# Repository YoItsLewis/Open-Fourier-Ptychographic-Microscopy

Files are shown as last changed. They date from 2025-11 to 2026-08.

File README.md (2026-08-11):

# Open Fourier Ptychographic Microscopy (OpenFPM)
**Open Fourier Ptychographic Microscopy (OpenFPM)** is a low-cost, modular, and open-source platform for Fourier Ptychographic Microscopy (FPM). It combines programmable LED illumination, 3D-printed optomechanical components, and computational reconstruction to enable high-resolution, wide field-of-view imaging using accessible hardware. The microscope architecture is based on version 7 of the OpenFlexure Project.

## Overview
Traditional FPM systems are typically implemented by retrofitting LED arrays onto commercial microscopes or through bespoke laboratory setups. These approaches can limit reproducibility, accessibility, and system-level optimisation. 

**OpenFPM addresses this by providing a fully integrated, purpose-built system**, in which optics, illumination, mechanics, and control software are designed to work together as a unified platform.

The system supports:
- Multi-angle programmable illumination
- Synthetic numerical aperture enhancement
- Digital aberration correction
- Multimodal imaging (e.g. brightfield, darkfield, Rheinberg contrast)

By leveraging open-source designs and widely available components, OpenFPM lowers the barrier to entry for computational microscopy in: 
- Research
- Education
- Resource-limited environments

## Pre-print Paper and Citation
Our 2026 bioRxiv preprint is available:

Walker, Lewis D., et al. 
"Open Fourier Ptychographic Microscopy (OpenFPM)" 
bioRxiv (2026): 2026-03

## Build Your Own OpenFPM system
<p align='center'>
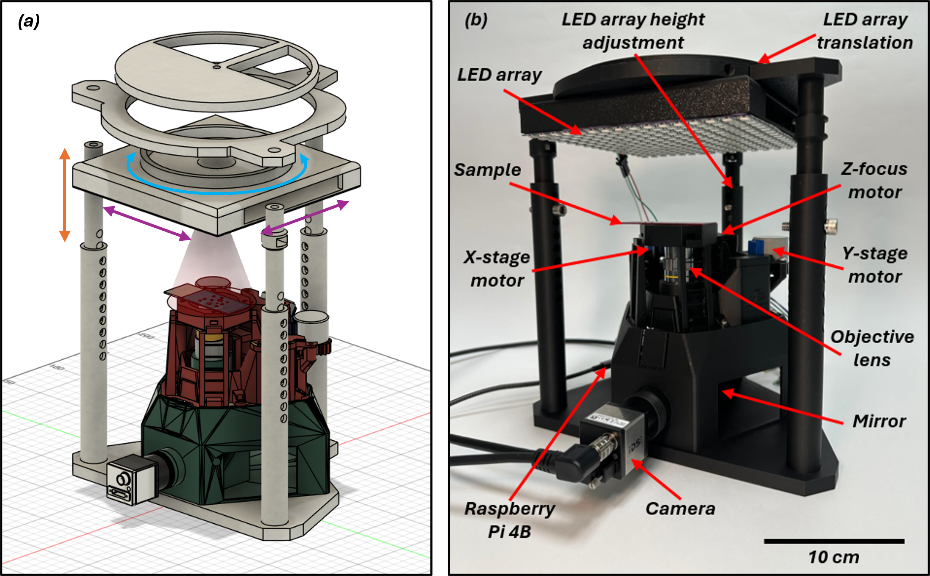
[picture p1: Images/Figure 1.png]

</p>

### Hardware

All 3D-printed components were fabricated using fused deposition modelling (FDM) with matte black polylactic acid (PLA) filament at a 0.4 mm layer height. Default print settings were used, with tree supports applied where required.

We found the [Bambu Labs P1S 3D Printer](https://uk.store.bambulab.com/products/p1s?id=578772891943051270) to be reliable for producing the components.

### Material Costs

Estimated material costs for building an OpenFPM system (excluding tools and general IT equipment):

| Parts | Purpose | Source | Quantity | Price (£) |
|-----|-----|-----|-----|-----|
| **Electronic Components** |
| Raspberry Pi 4 Model B Starter Kit (1GB) | Microcomputer for controlling the microscope | [The Pi Hut](https://thepihut.com/products/raspberry-pi-starter-kit?srsltid=AfmBOoqbFpfRUvJug9U0IUKZXNz2ZsnnAsgzD-O2ssctK8kTpJ7MEXZv&variant=41173475754179) | 1 | ~£57 |
| 28BYJ-48 5V Stepper Motor + Driver Board | Objective focus and X-Y sample translation | [Amazon](https://www.amazon.co.uk/GeeekPi-Stepper-28BYJ-48-Uln2003-Compatible/dp/B087BYKB6T/ref=sr_1_5?dib=eyJ2IjoiMSJ9.tpKbALur4RZR5JjIbrZBahg9M0IhaDgmiF7VwBWE_2lsTL00-iRC6xXIvnyfChnaYqPoV9Gr50YNRAiiWclIkc7meNSNdmMirNrMPg_gOMrreA9ZntPfVBQ38vUR9fwi93x8wK9a9-xv7wTnYonW1l5yaqqH8dDyoqPMSYfvQgSfoi7agcg3Q4DXaJho1xlHV60y0XfS1d2ZRnEMOHDfPPFEu1HbcgymNHAHrIat6Jai5Hy_woxu5Wi1DnVFxtKRGXrG9qPlf7OP2aix-48fc58KT13RH6gw9dvW76QfDPg._fRZJClR4FFzt0LQ7L6sIkDKB9mwDvTVIwPNkDp-gEc&dib_tag=se&keywords=28byj-48&qid=1773853029&sr=8-5) | 1 | ~£16 |
| WS2812B RGB 16x16 LED Array | Microscope illumination source | [Amazon](https://www.amazon.co.uk/BTF-LIGHTING-Individual-Addressable-Flexible-Controllers/dp/B088K1JH6X/ref=sr_1_4?crid=1TDCCR1PVHEZI&dib=eyJ2IjoiMSJ9.BlBbfjaxQD81QRlFc0RoykGyvNqepSEBWBUXSh5dhH8Izaq5I3eHLzQNwcP58zJ_g5KJcmAz3sXc5WHSyN3tFMFqY885Ji_6wpYi1NJLEjbaBzJerwrchq3Al4w8YoxB44xzRurl0KOIqh-5-MLe0q_TGN8MHpB84Jl03lWM88kHzF7ABw2D_dwZOi-cpTNZaxy0pDkv0YXhD4YJeiqqaFl3o17sfhu8GvuNenMw-57pwuYcKO2ADKH5zCnCxQtYtTxeWC3wZmMnI0opGIlZ_wdnl_BQJ4-rvEX3ecfqd6A.ILqKG4o1fKNMmcr2hGjSUMYwglu0uDxfSaB0AR59xHk&dib_tag=se&keywords=led%2Barray&qid=1773851490&s=kitchen&sprefix=led%2Barray%2Ckitchen%2C222&sr=1-4&th=1) | 1 | ~£20 |
| Breadboard and Jumper Wires Kit | Wiring for connecting the microcomputer to the LED array + Motors | [Amazon](https://www.amazon.co.uk/HUAREW-Breadboard-Jumper-Include-Points/dp/B0B5TCKTQH/ref=sr_1_4_sspa?crid=314GBN29Q2J8Q&dib=eyJ2IjoiMSJ9.Vdt6Ti1-DwLZVl5Jd0sx8KltvLq3nGuI3O04CljjMjJocwzI61z4BB8c2a6rk0_9YaFVxERGaFBxc0RotFdqHZlzmlmX0Bp-n_uB6315HeygDOw5QO-6VEgO0mXQDr6mDOv0xnvJ4iTOfin41Tiof4i14ME5M7KTHz8C8Um_5GoPDg4zJ0oTeF5nXYIctct5aNjJOGhbHd2HcHNLUlW4ldUbhzsSWMjL6NehSN-cv4WeTMtcGuIXSskGMmhh-G8XeVrsZpbGsGJ7sSK_u00s51z4WUAfj5VZ1297tedRsZ0.nCFNU3pLaWR8MUiCFS34yDLuV5LY6le9KtSD54dFcJU&dib_tag=se&keywords=electronics+breadboard&qid=1773851170&sprefix=electronics+breadboard%2Caps%2C253&sr=8-4-spons&aref=b7CJuJoBlm&sp_csd=d2lkZ2V0TmFtZT1zcF9hdGY&psc=1) | 1 | ~£13 |
| Monochromatic Camera (c-mount) | Acquiring image data | [Edmund Optics](https://www.edmundoptics.co.uk/c/cameras/1012/#27915=27915_s%3AC-Mount&397021=397021_s%3AMonochrome&29401=29401_s%3AIDS) | 1 | ~£300 (Based on iDS camera) |
| USB 3.0 A to Right-Angle Micro B Cable | Provides power to the camera and transfers image data | [Thorlabs](https://www.thorlabs.com/item/CABU32) | 1 | ~£17 |
| 8 Pin Hirose Camera Cable | Cable for triggering camera from microcomputer | [Amazon](https://www.amazon.co.uk/Alvins-Cables-HR25-7TP-8S-Imaging-Industrial/dp/B08FD6B262?source=ps-sl-shoppingads-lpcontext&ref_=fplfs&th=1) | 1 | ~£25 |
| **Total** |||| ~ £448 |
| **Optomechanical Components** |
| Finite Conjugate Objective Lens | Objective lens for microscope | [Edmund Optics](https://www.edmundoptics.com/f/commercial-grade-standard-microscope-objectives/12253/) | 1 | ~£152 (10x/0.25 Plan) |
| ⌀1" Protected Aluminum Mirror | Redirect light path onto camera sensor | [Thorlabs](https://www.thorlabs.com/item/PF10-03-G01) | 1 | ~£50 |
| M6 x 16 mm | Screw for combining the LED box hat to the LED box holder | | 1 | |
| M6 x 20 mm | Screws, washers and nuts for combining external post to microscope base plate | | 3 | |
| M6 x 25 mm | Screws for pin and hole system | | 3 | |
| M6 x 30 mm | Screws and nuts for combining internal post to LED canopy | | 3 | |
| **Total** |||| ~£202 |
| **Overall Total** |||| ~£650 |

## Assembly Instructions

OpenFPM assembly guide can be found [here](https://github.com/YoItsLewis/Open-Fourier-Ptychographic-Microscopy/tree/main/Assembly%20Instructions).

OpenFlexure microscope assembly instructions can be found [here](https://build.openflexure.org/openflexure-microscope/v7.0.0-beta5/high_res_microscope.html). 

## Software

The OpenFPM software provides control of illumination, acquisition, and mechanical positioning via a Raspberry Pi-based graphical user interface (GUI).
- LED control using WS2812B NeoPixel interface
- Motor control for focus and stage translation
- Programmable illumination sequences for FPM acquisition

[NeoPixel](https://core-electronics.com.au/guides/fully-addressable-rgb-raspberry-pi/) setup guide.

OpenFPM [Control software](https://github.com/YoItsLewis/Open-Fourier-Ptychographic-Microscopy/tree/main/Software).

## Datasets

Due to file size constraints, example datasets are hosted externally:
- Siemen star (Red illumination) 
- Blood smear (RGB 3-channel illumination)

Available via the [Strathclyde Data Repository](https://pureportal.strath.ac.uk/en/persons/lewis-walker-2/).

## License

Original OpenFPM software, documentation, and custom files in this repository are released under the MIT License unless otherwise stated.

Certain hardware components are based on or compatible with the OpenFlexure Project. Original OpenFlexure hardware designs are licensed separately under CERN-OHL-S.

## Acknowledgements

OpenFPM builds upon foundational contributions from the Fourier Ptychographic Microscopy community and the OpenFlexure Project. OpenFlexure source files and licence information: https://gitlab.com/openflexure

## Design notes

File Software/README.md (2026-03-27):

# Software

This folder contains the software used to operate the OpenFPM microscope system, including microscope control, illumination and camera sequencing, motorised positioning, and optical alignment support.

### OpenFPM Control GUI

The OpenFPM control software provides a graphical user interface (GUI) for controlling the programmable LED illumination and microscope translation hardware.

### Features

#### LED Illumination Control

- Support for a 16x16 WS2812B LED array
- Adjustable:
  - LED colour
  - LED brightness
- Visual 16x16 LED grid interface

#### Timing

- User-defined timing parameters for image acquisition:
  - Exposure time (ms) - LED on duration
  - Capture time (ms) - LED off duration

#### Illumination Patterns

Predefined and custom illumination patterns are supported.

- Hold modes
  - Brightfield (BF)
  - Darkfield (DF)
- Triggered acquisition modes
  - Central 9 LEDs (3 LED diameter circle)
  - 69  LEDs (9 LED diameter circle)
  - 177 LEDs (15 LED diameter circle)

Users may also define custom LED illumination patterns directly in the code.

#### Motor Control

Integrated manual control of microscope motion:
- Z-axis focus
- X-axis stage translation
- Y-axis stage translation

#### Image of on-screen GUI

<p align='center'>
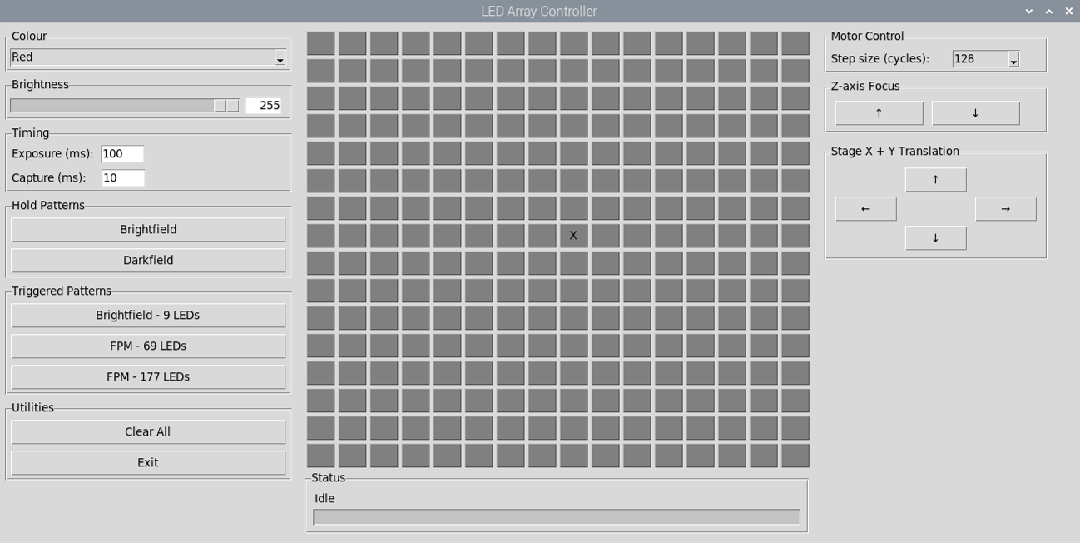
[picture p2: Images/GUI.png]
  
</p>

### Live FFT Alignment Support

OpenFPM incorporates a translational LED illuminator, allowing the user to manually align the LED array with the microscope optical axis for improved reconstruction quality.

To support this process, the system uses a high-contrast sample and live Fourier-space observation of the coherent brightfield passbands. This enables the user to visually assess whether the central LED is correctly aligned to the optical axis.

This alignment workflow is supported using a live on-screen FFT display in FIJI, adapted from the macro shared by Nicolás De Francesco [1].

Live FFT visualisation helps the user:
- Identify off-axis illumination
- Observe coherent passband displacement
- Manually correct LED array alignment
- Improve reconstruction consistency and quality

Below is an example showing the central LED:
- Off-axis (uncorrected) position
- On-axis (corrected) psoition

<p align='center'>
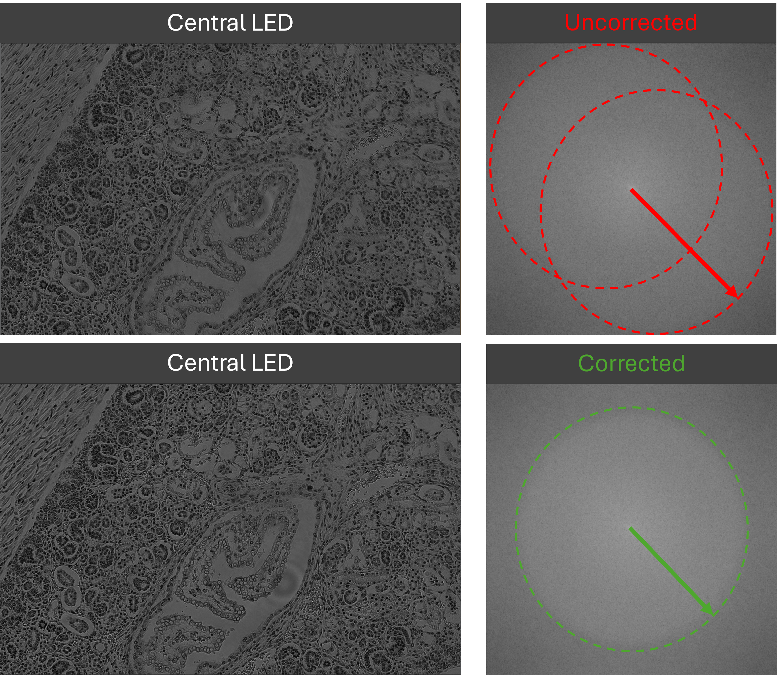
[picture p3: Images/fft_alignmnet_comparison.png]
  
</p>

### FIJI Macro Reference
Nicolás De Francesco,
“Is live FFT of an ROI on screen possible?”
Image.sc Forum, November 2019.
https://forum.image.sc/t/is-live-fft-of-an-roi-on-screen-possible/31026/4
Accessed: March 2026.

### Notes
- This software was developed for use with the OpenFPM hardware platform and may require modification for alternative hardware configurations.
- Custom illumination sequences and acquisition routines can be adapted within the source code depending on the desired imaging protocol.

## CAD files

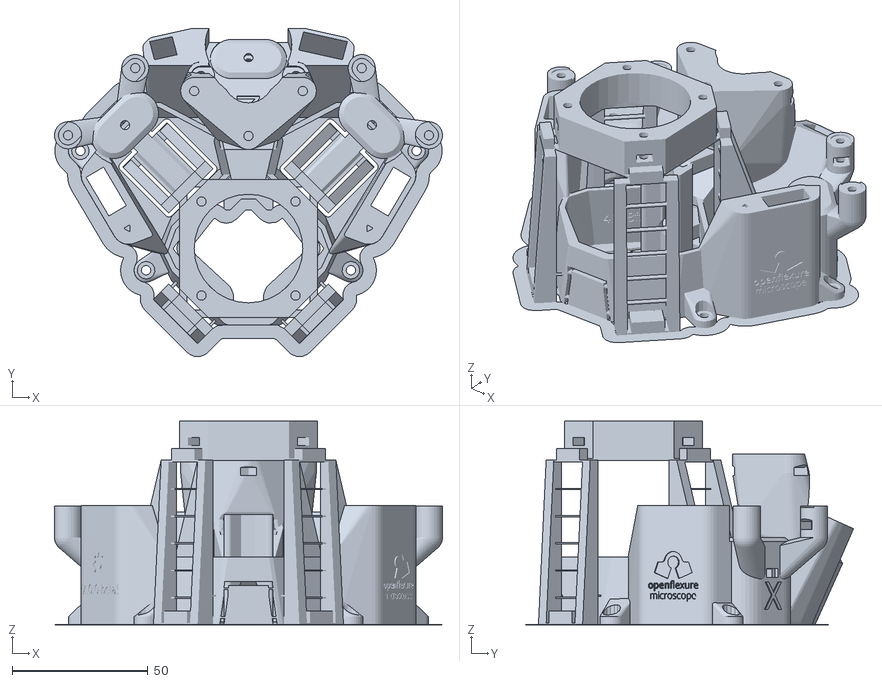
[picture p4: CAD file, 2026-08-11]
3D Printing Files/STL Files/OpenFlexure_main_body.stl
142.9 x 120.9 x 75.0

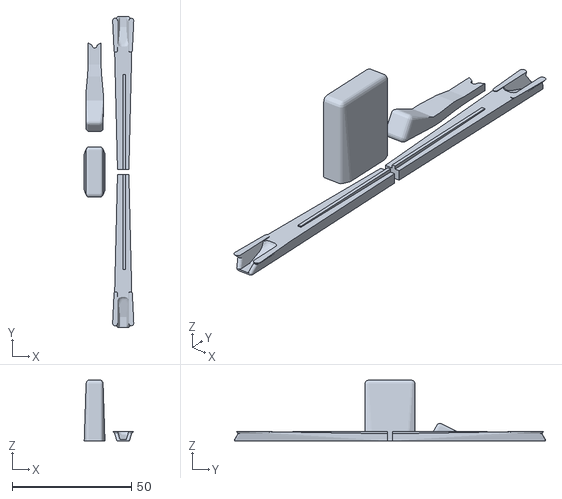
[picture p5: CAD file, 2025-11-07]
3D Printing Files/STL Files/OpenFlexure_actuator_assembly_tools.stl
20.8 x 130.5 x 25.5

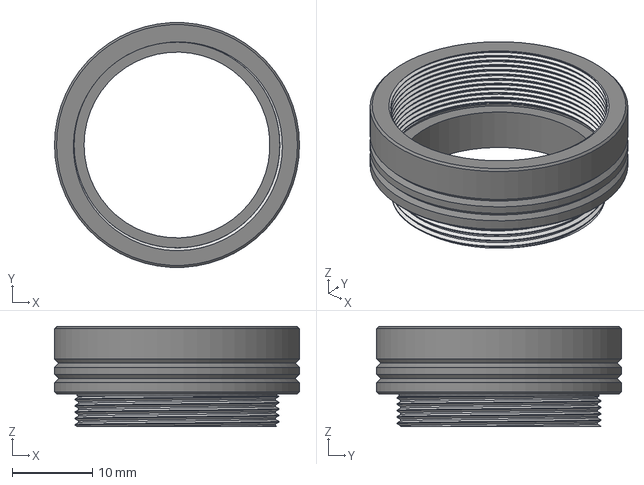
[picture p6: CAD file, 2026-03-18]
3D Printing Files/STEP Files/Camera Adapter.step
30.5 x 30.4 x 12.4 mm

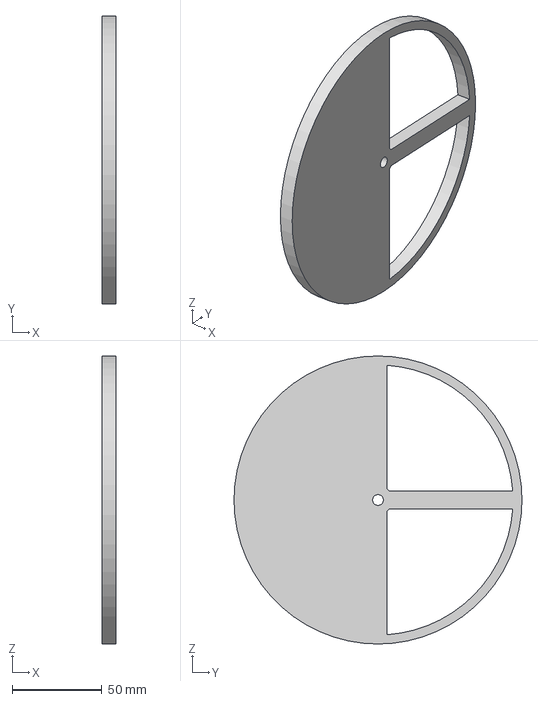
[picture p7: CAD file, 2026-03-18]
3D Printing Files/STEP Files/LED Box Hat.step
8.00 x 160.0 x 160.0 mm

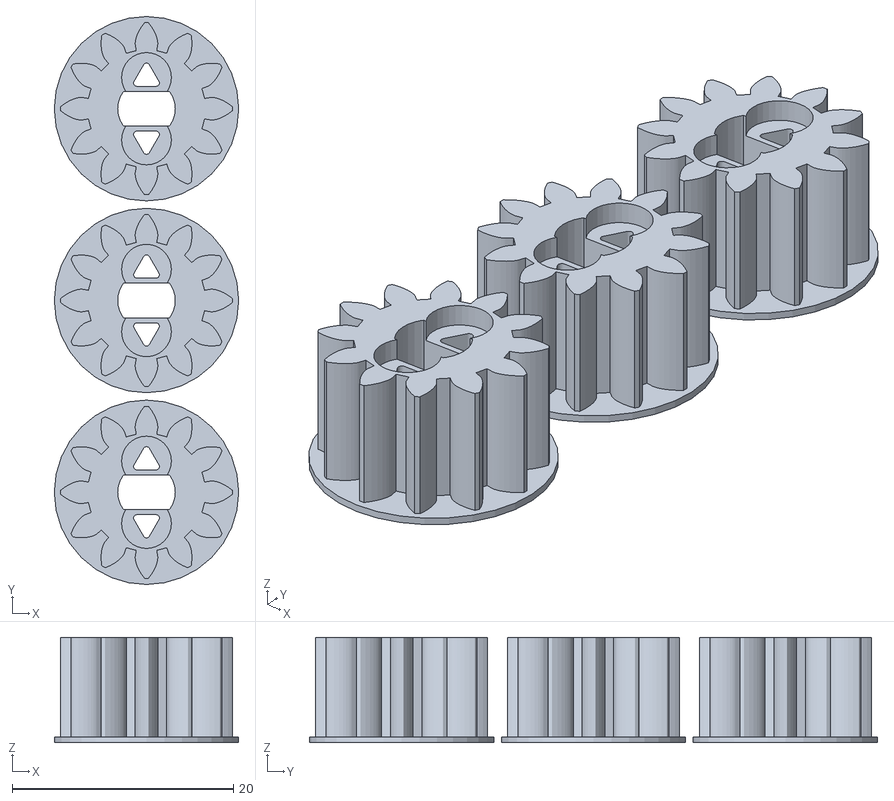
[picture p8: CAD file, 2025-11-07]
3D Printing Files/STL Files/OpenFlexure_small_gears.stl
16.7 x 51.3 x 9.50

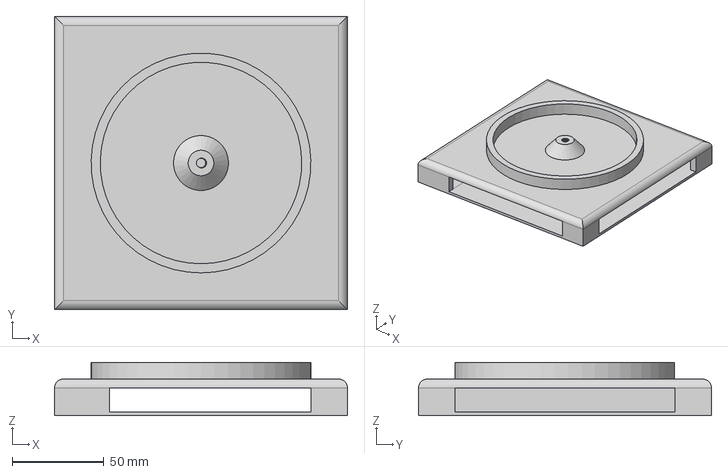
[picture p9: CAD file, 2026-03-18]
3D Printing Files/STEP Files/LED Box Holder.step
160.0 x 160.0 x 29.0 mm

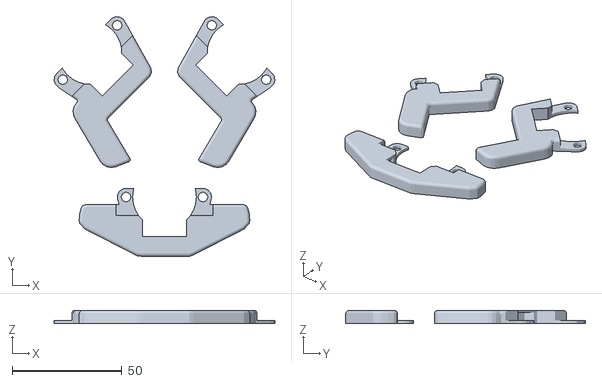
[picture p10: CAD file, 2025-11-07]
3D Printing Files/STL Files/OpenFlexure_cable_tidies.stl
100.6 x 109.1 x 6.03

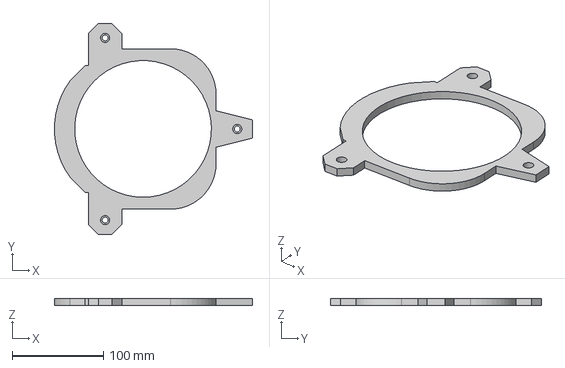
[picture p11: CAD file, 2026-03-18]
3D Printing Files/STEP Files/LED Canopy.step
217.3 x 232.0 x 8.00 mm

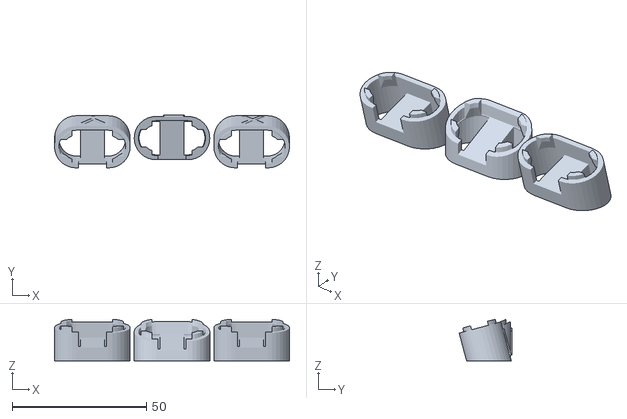
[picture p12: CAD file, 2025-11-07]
3D Printing Files/STL Files/OpenFlexure_feet.stl
87.6 x 19.7 x 15.5

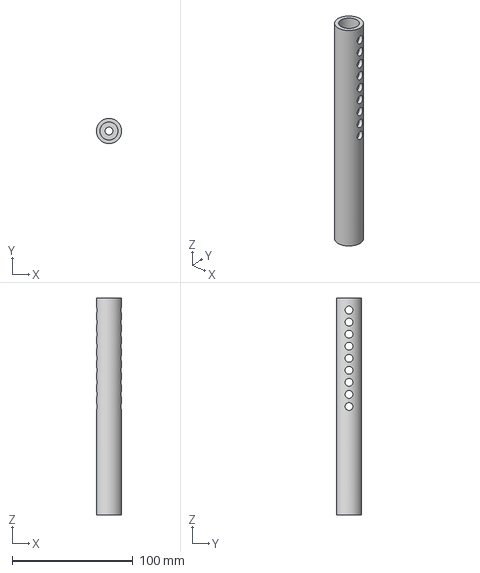
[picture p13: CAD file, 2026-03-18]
3D Printing Files/STEP Files/External Post.step
21.0 x 21.0 x 180.0 mm

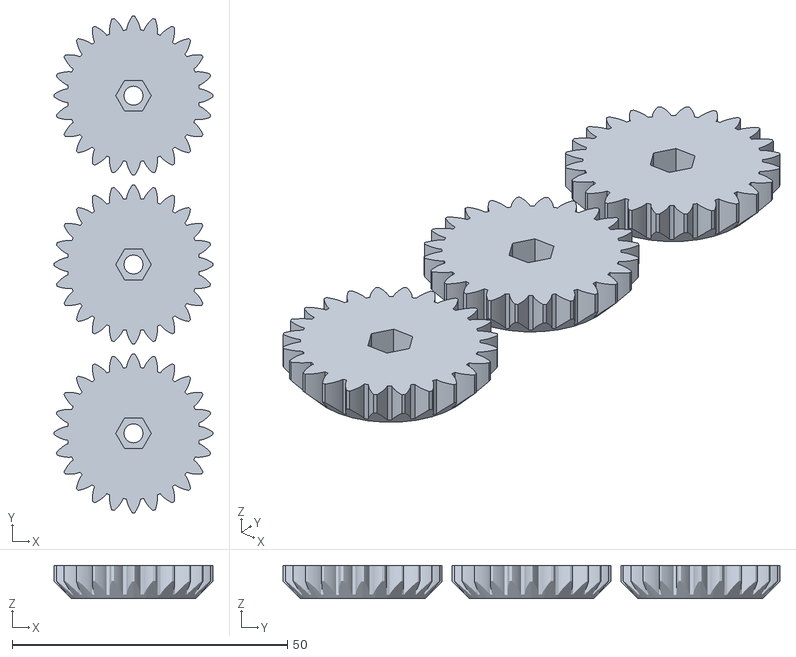
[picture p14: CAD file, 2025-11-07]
3D Printing Files/STL Files/OpenFlexure_large_gears.stl
28.9 x 90.2 x 6.00

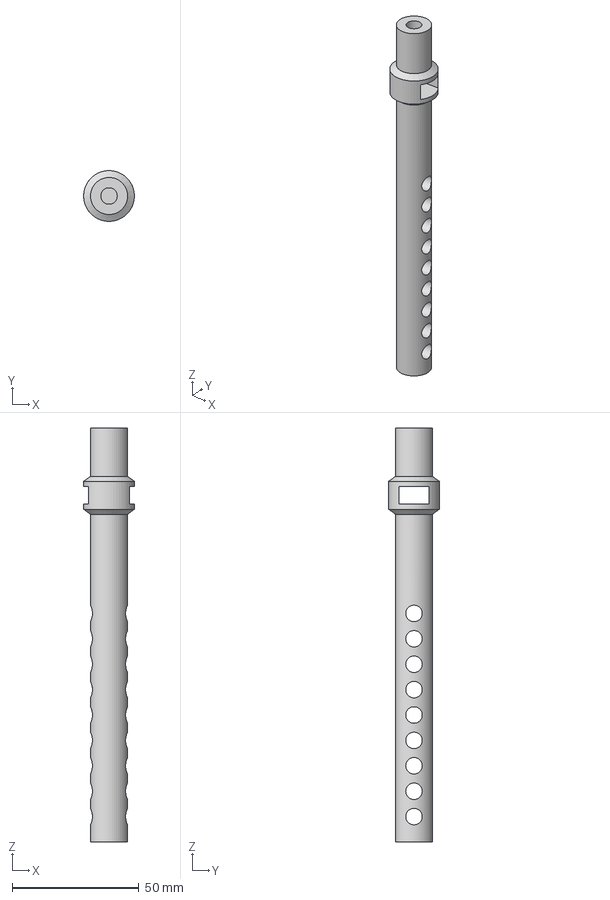
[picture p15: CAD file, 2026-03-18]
3D Printing Files/STEP Files/Internal Post.step
20.0 x 20.0 x 163.0 mm

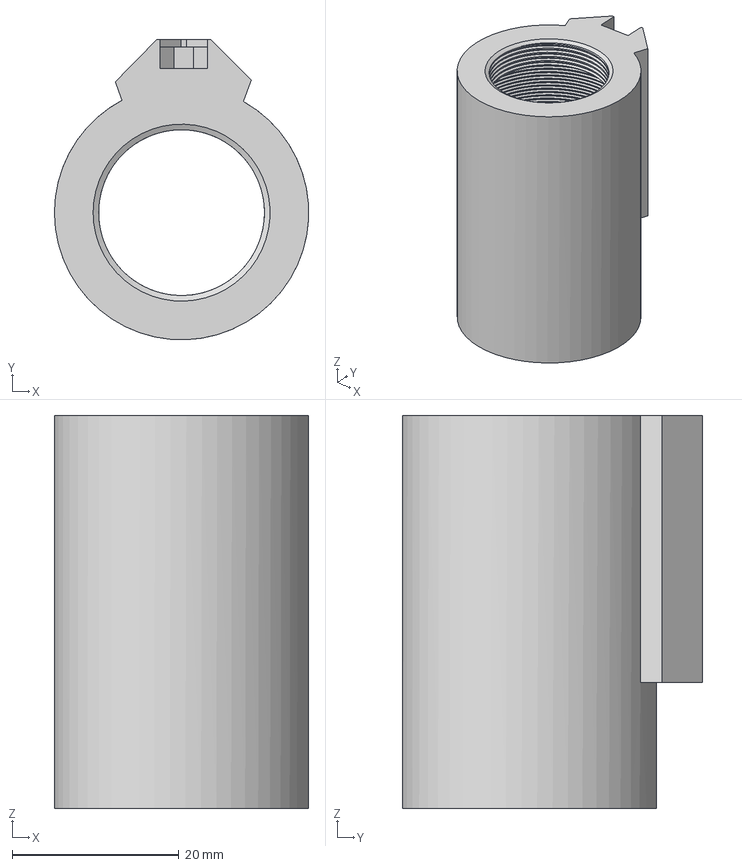
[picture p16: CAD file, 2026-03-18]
3D Printing Files/STEP Files/Objective Lens Holder.step
30.5 x 36.0 x 47.1 mm

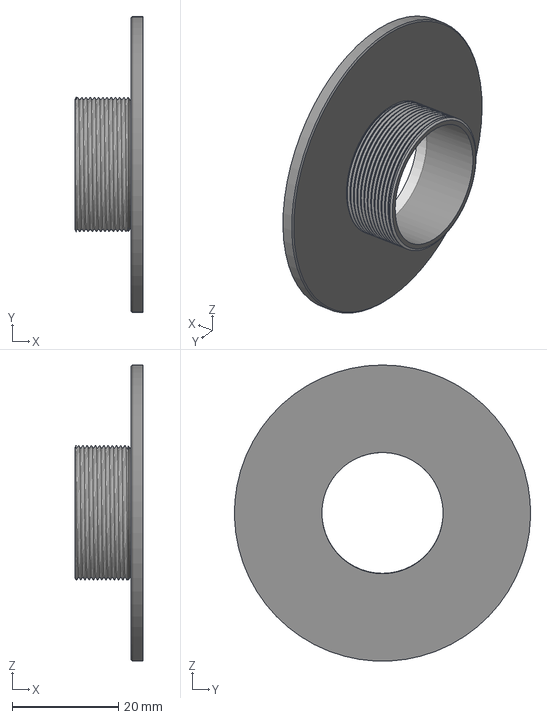
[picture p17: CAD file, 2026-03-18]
3D Printing Files/STEP Files/C mount Mirror Cover.step
12.9 x 55.9 x 55.8 mm

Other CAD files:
3D Printing Files/STEP Files/Microscope Base Plate.step
3D Printing Files/STEP Files/OpenFlexure Stand with Mirror Holder.stl
3D Printing Files/STEP Files/Hex Nut Tool.step
3D Printing Files/F3D Files/C mount Mirror Cover.f3d
3D Printing Files/F3D Files/Camera Adapter.f3d
3D Printing Files/F3D Files/External Post.f3d
3D Printing Files/F3D Files/Hex Nut Tool.f3d
3D Printing Files/F3D Files/Internal Post.f3d
3D Printing Files/F3D Files/LED Box Hat.f3d
3D Printing Files/F3D Files/LED Box Holder.f3d
3D Printing Files/F3D Files/LED Canopy.f3d
3D Printing Files/F3D Files/Microscope Base Plate.f3d
3D Printing Files/F3D Files/Objective Lens Holder.f3d
3D Printing Files/F3D Files/OpenFlexure Stand with Mirror Holder.f3d
3D Printing Files/STL Files/C mount Mirror Cover.stl
3D Printing Files/STL Files/Camera Adapter.stl
3D Printing Files/STL Files/External Post.stl
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

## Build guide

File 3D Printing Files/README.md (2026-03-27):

# 3D Printing Files

This directory contains the complete set of 3D design files for the OpenFPM microscope components. The files are provided in multiple formats to support a range of workflows, from direct 3D printing to further design modification and customisation.

### Folder Structure

The files are organised into three subfolder:

- F3D/
  - Native Autodesk Fusion 360 design files.
  - These are fully parametric and intended for users who wish to modify or adapt the designs.

- STEP/
  - Standard CAD exchange files (.step).
  - Suitable for use in a wide range of CAD software for inspection, modification, or integration into other assemblies.

- STL/
  - Mesh files for direct 3D printing.
  - These are ready to slice and can be used with most 3D printing software. (e.g. Bambu Studio, LycheeSlicer).

### Usage 

- For direct printing, use the files in the STL/ folder.
- For design modification or customisation, use the F3D/ or STEP/ files depending on your preferred CAD software.

### Notes

- All  components are designed to be compatible with the OpenFPM system architecture.
- Print settings (e.g. material, infill, layer height) may be adjusted depending on your printer and desired mechanical performance.
- Some parts may require support structures depending on orientation, this can usually be auto-checked in slice software.

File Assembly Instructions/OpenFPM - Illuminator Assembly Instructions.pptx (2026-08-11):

## OpenFPM: Illuminator Assembly Instructions

- Lewis Walker
- University of Strathclyde, Glasgow, Scotland
- Last Edited: 11th August 2026

## Components

Here we provide a list of the components (and their quantity) required to assemble the illuminator:

3D Printed Components:
- External post (x3)
- Internal post (x3)
- LED box hat (x1)
- LED box holder (x1)
- LED canopy (x1)
- Microscope base plate (x1)
- Hex Nut Tool (x1) - Tool
Metal Components:
- M6x16 mm bolt (x1)
- M6x20 mm bolt (x3)
- M6x25 mm bolt (x3)
- M6x30 mm bolt (x3)
- M6 nuts (x6)
Consumables + Tools
- Super-glue
- 5 mm hex key M6 tool
- 2.5 mm hex key M3 tool

## Parts I

From Left to Right on the image
Top:
- LED box hat (x1)
- LED box holder + LED array (under) (x1)
- Internal post (x3)
- External post (x3)
Bottom:
- LED canopy (x1)
- Microscope base plate (x1)
- Hex Nut Tool (x1)

## Parts II

Consumables + Tools:
- Super-glue
- 5 mm hex key M6 tool
- 2.5 mm hex key M3 tool
Optional:
- 3D printed bolt measuring tool
Metal components:
- M6 nuts (x6)
- M6x30 bolt mm (x3)
- M6x25 bolt mm (x3)
- M6x20 bolt mm (x3)
- M6x16 bolt mm (x1)

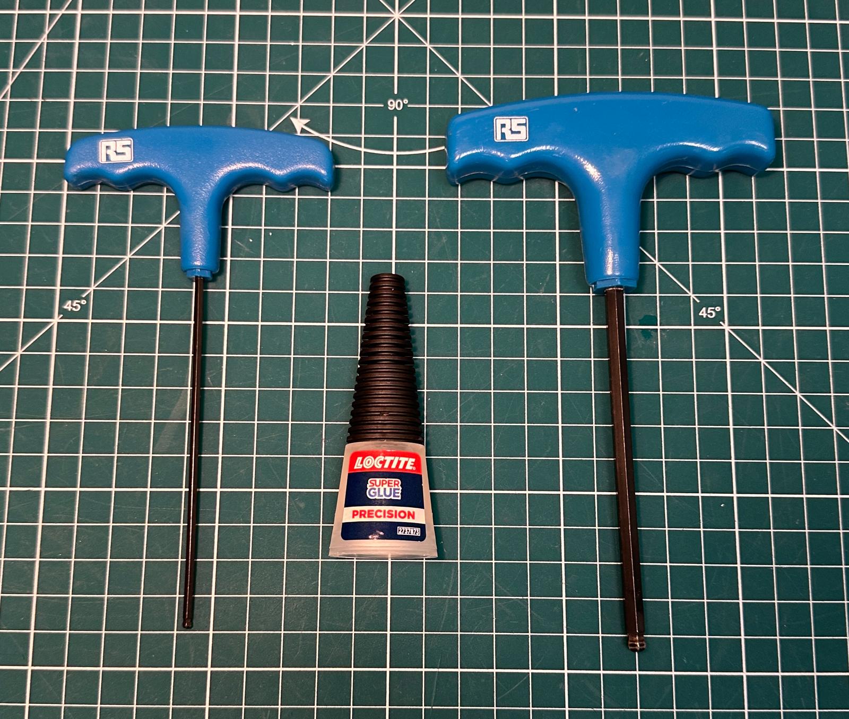
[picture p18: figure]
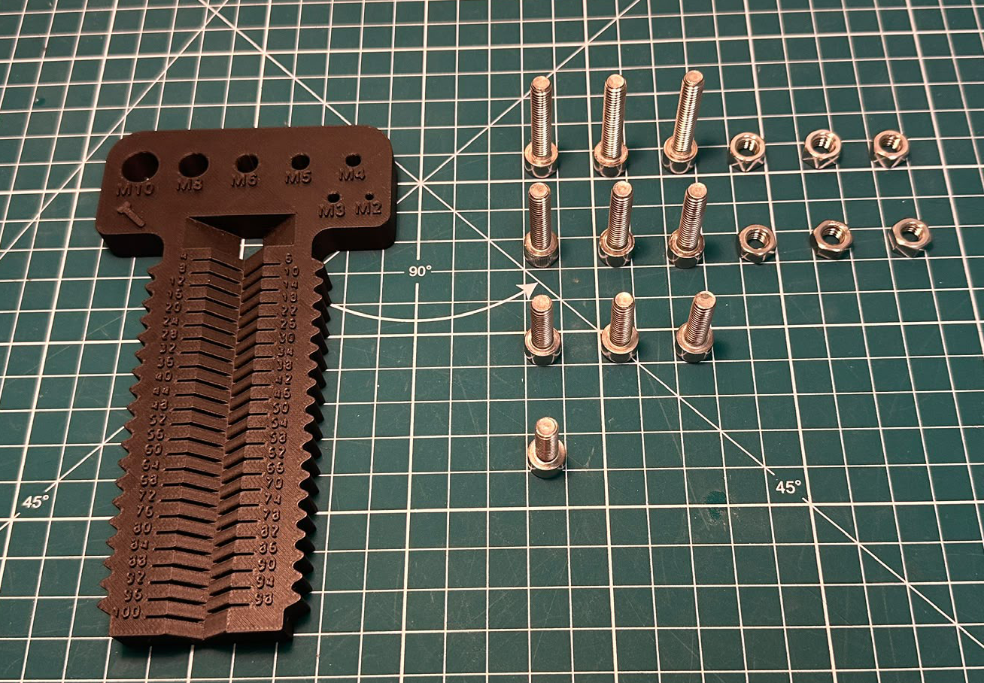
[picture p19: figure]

## Step 1

What you will need:
- LED box holder
- LED array
- Super-glue
TODO:
1. Thread LED wires through the square holes in the 3D printed box. Position the LED array to the edges of the box and superglue along the edges and the middle to ensure good contact.
2. Place upside-down on a flat surface and leave to dry.

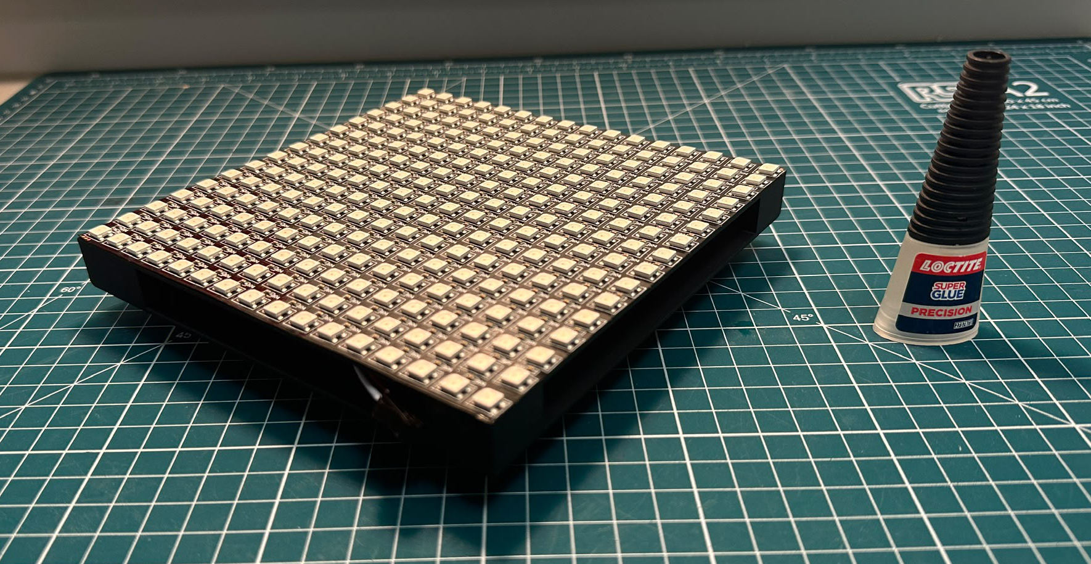
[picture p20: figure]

## Step 2(a)

What you will need:
- External posts
- Microscope base plate
- Hex nut tool
- M6x25 mm bolts (x3)
- M6 nuts (x3)

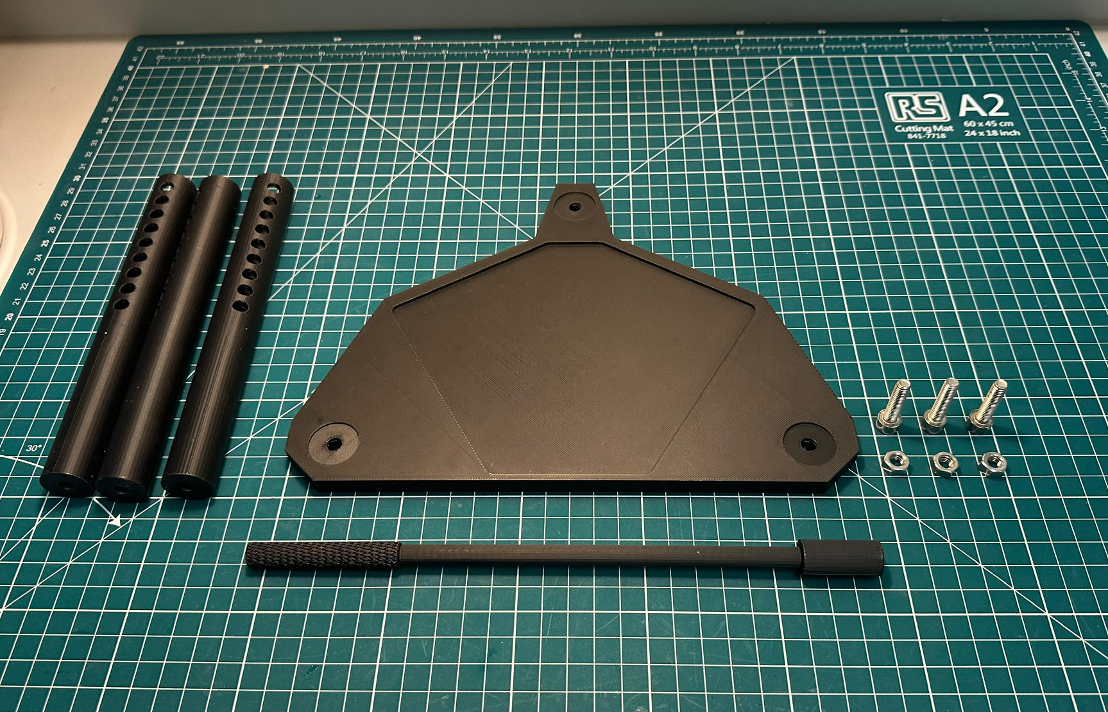
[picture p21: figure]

## Step 2(b)

TODO:
1. Place the 3 M6x25 mm bolts through the bottom of the microscope base plate.

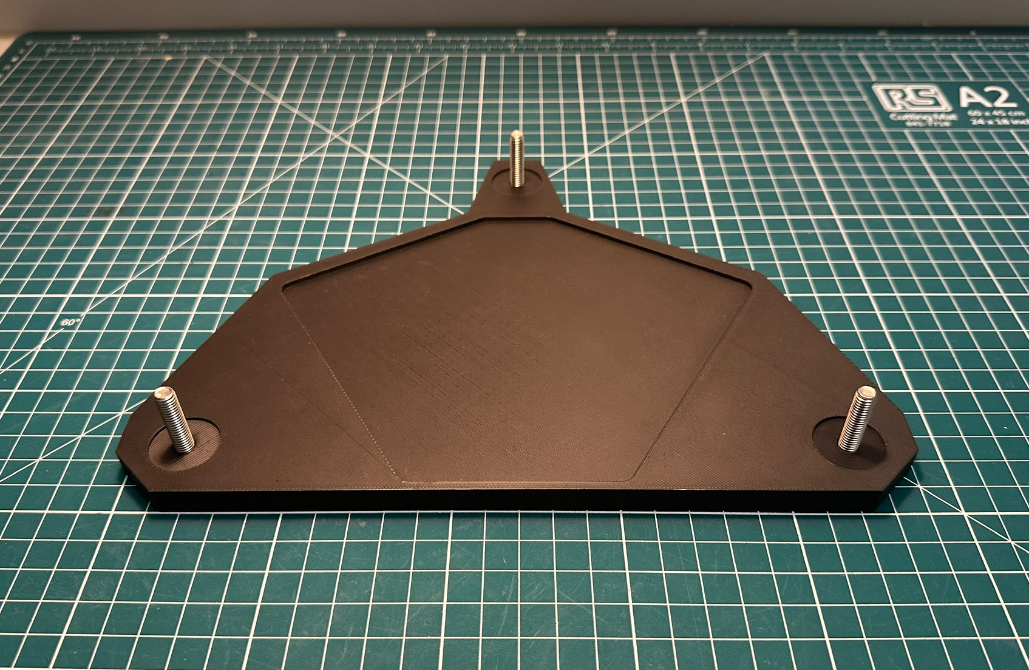
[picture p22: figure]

## Step 2(c)

TODO:
1. Next, place one of the external posts onto a bolt.

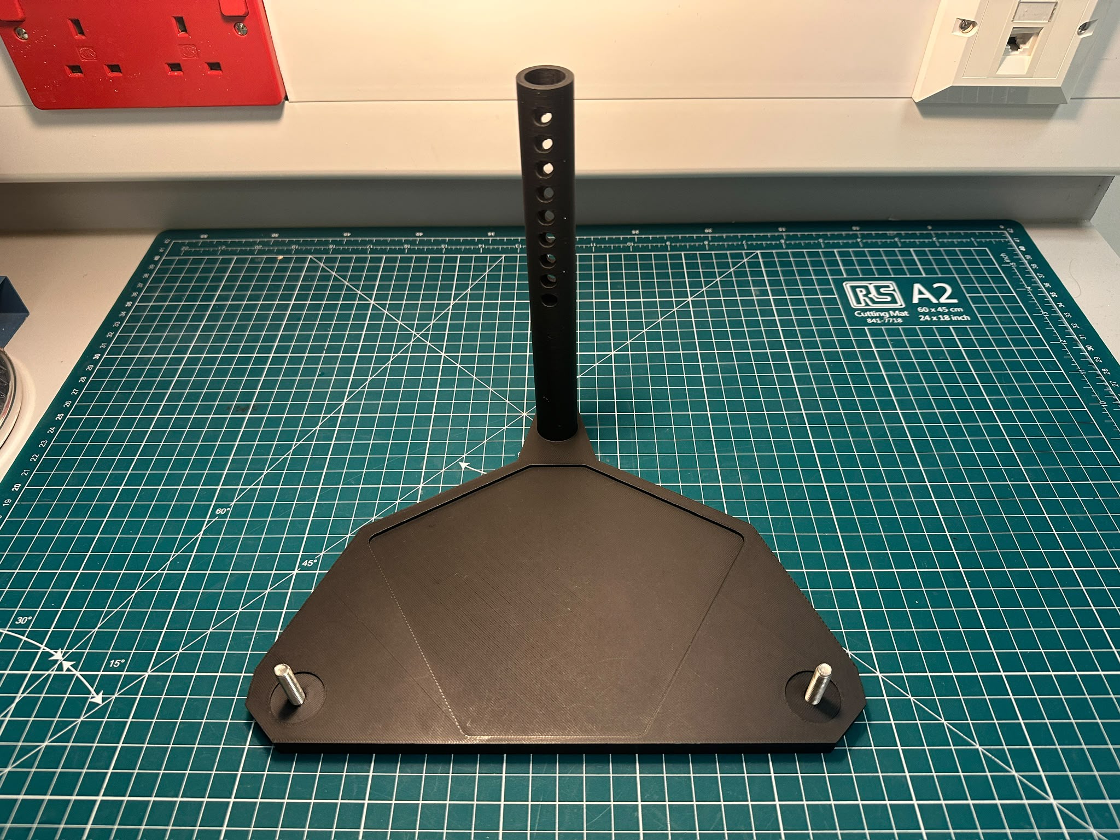
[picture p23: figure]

## Step 2(d)

TODO:
1. Using the hex nut tool, carefully screw an M6 nut onto the bolt to attach the external post
Tip:
- Place nut and hex tool into external post to ensure good contact before placing the post onto the bolt and threading.

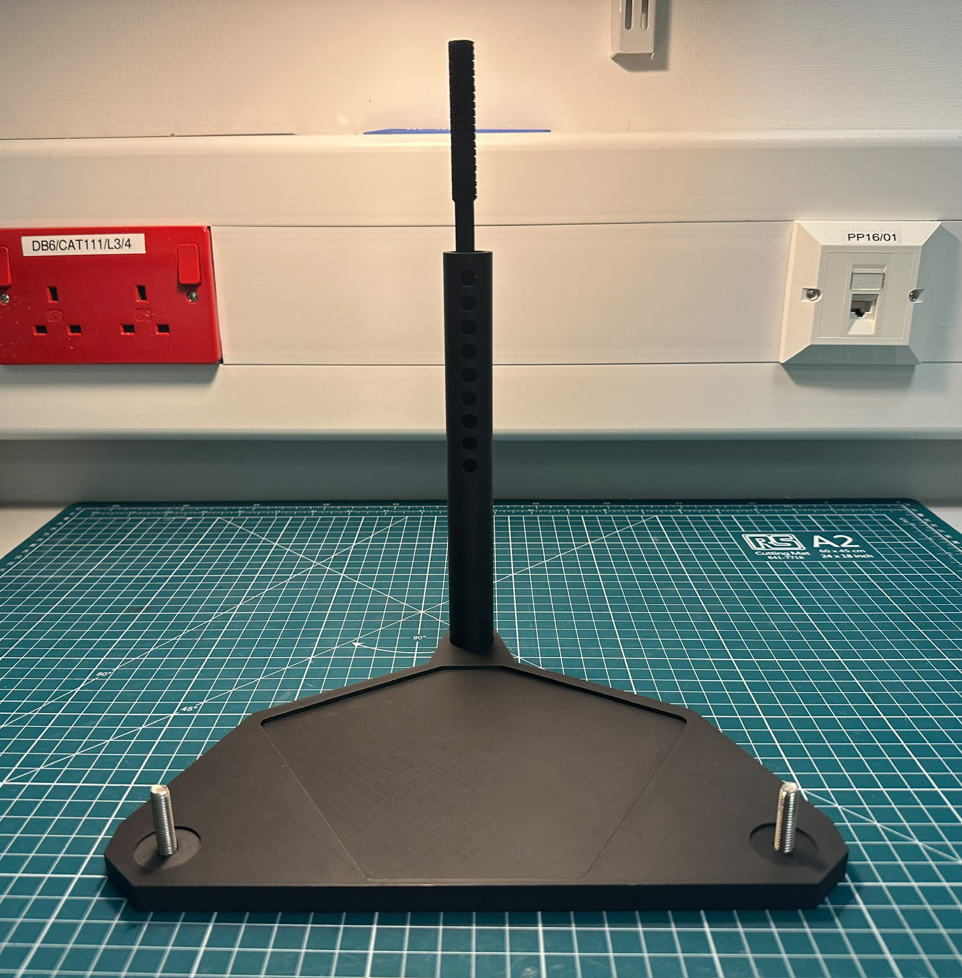
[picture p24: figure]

## Step 2(e)

TODO:
1. Repeat Step 2 (c) and (d) for the remaining two external posts.
2. Each post can be twisted into positions (shown on the image) and retightened if required.

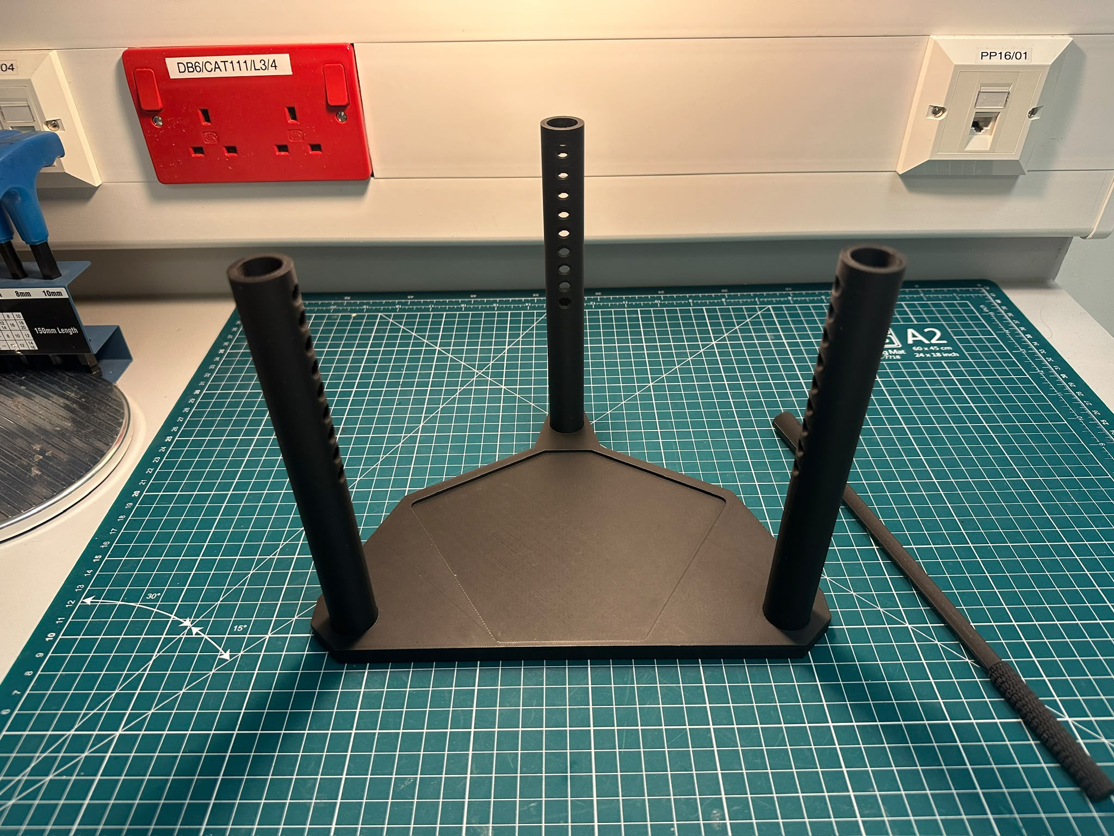
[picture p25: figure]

## Step 3(a)

What you will need:
- Internal posts
- LED canopy
- M6x30 mm bolts (x3)
- M6 nuts (x3)
Tools:
- 5 mm hex key M6 tool
- 2.5 mm hex key M3 tool

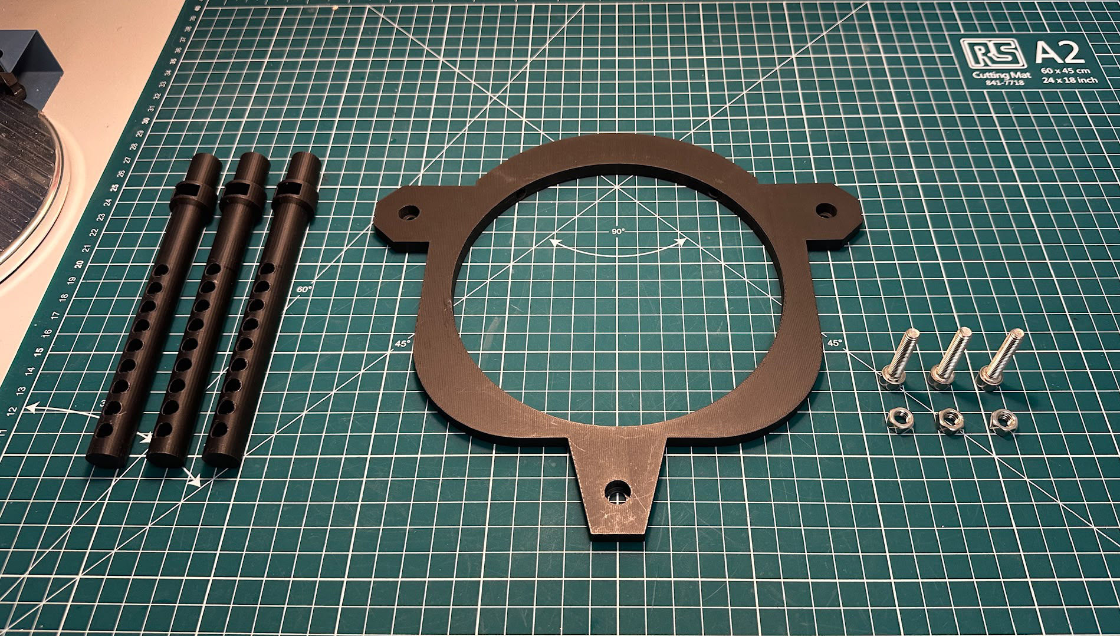
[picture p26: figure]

## Step 3(b)

TODO:
1. Place the 3 M6x30 mm bolts through the top of the LED canopy, so that the top of each bolt is flush to the surface.

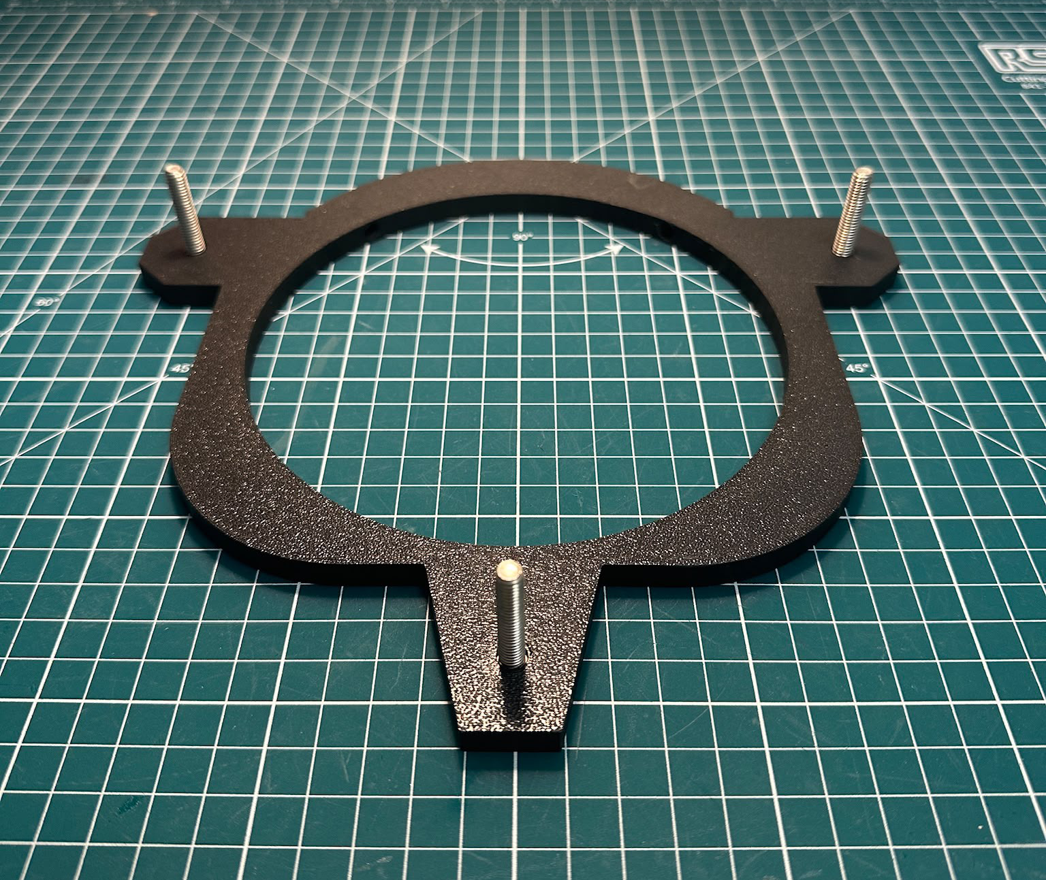
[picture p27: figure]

## Step 3(c)

TODO:
1. Next, carefully place an M6 nut into the slot of the Internal posts

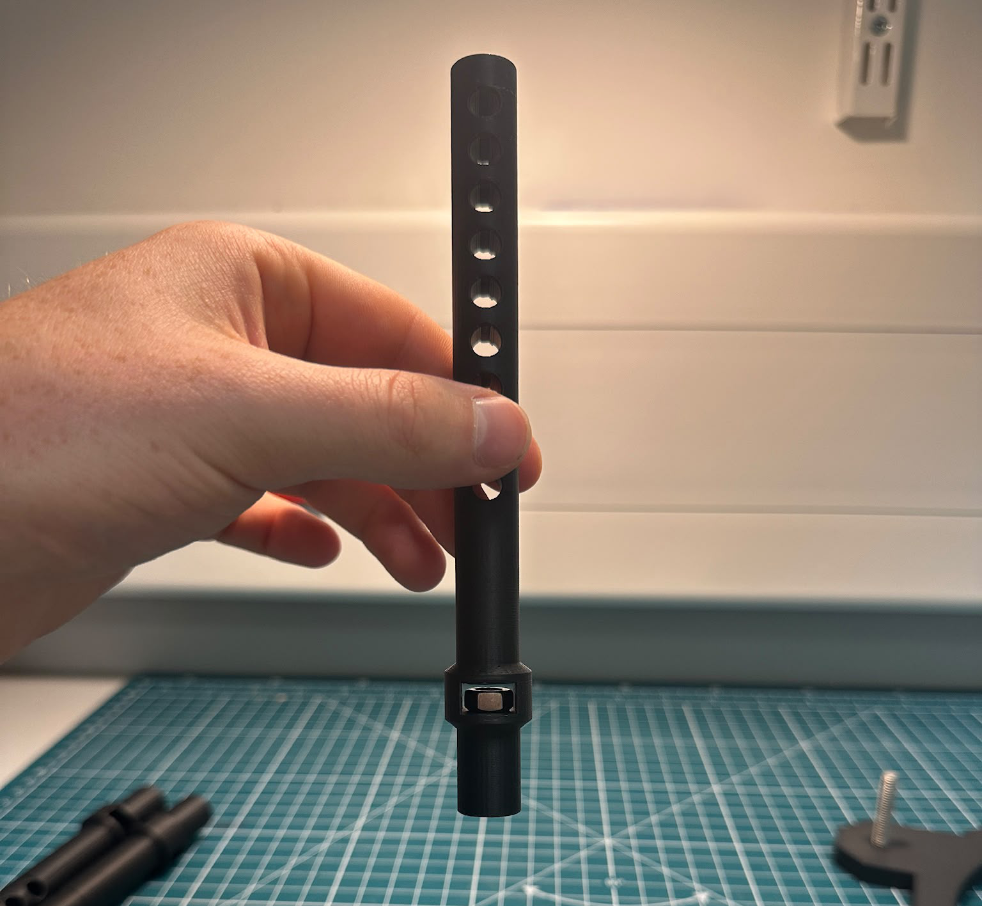
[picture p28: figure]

## Step 3(d)

TODO:
1. Afterwards, connect one the internal post to one of the bolts attached to the LED canopy.

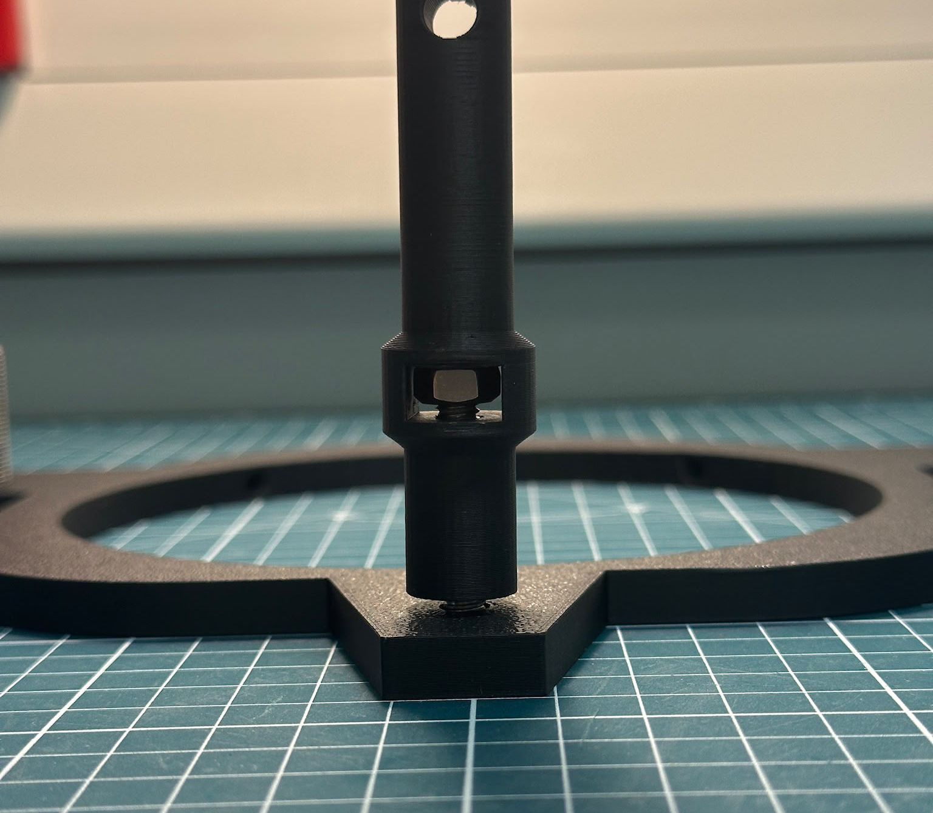
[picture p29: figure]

## Step 3(e)

TODO (Tricky):
1. A 2.5 mm hex key M3 tool (or similar) can be used to wedge the M6 nut in place.

## Step 3(f)

TODO (Tricky):
1. Once the M6 nut is securely wedged, a 5 mm hex key M6 tool can be used to tighten the M6 bolt.
Tip:
Use both hands to secure the nut and tighten the bolt simultaneously, you can also grip onto the post.

## Step 3(g)

TODO:
1. Once tightened, visually inspect the assembly. The post should look like this.

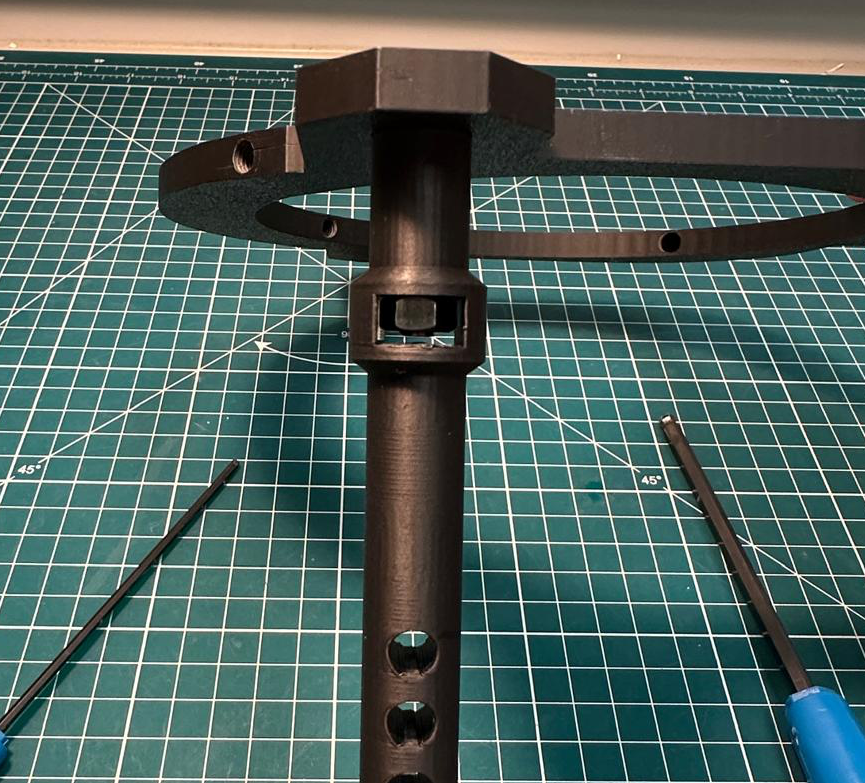
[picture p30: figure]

## Step 3(h)

TODO:
1. Repeat Step 3 (c-g) for the remaining two internal posts.

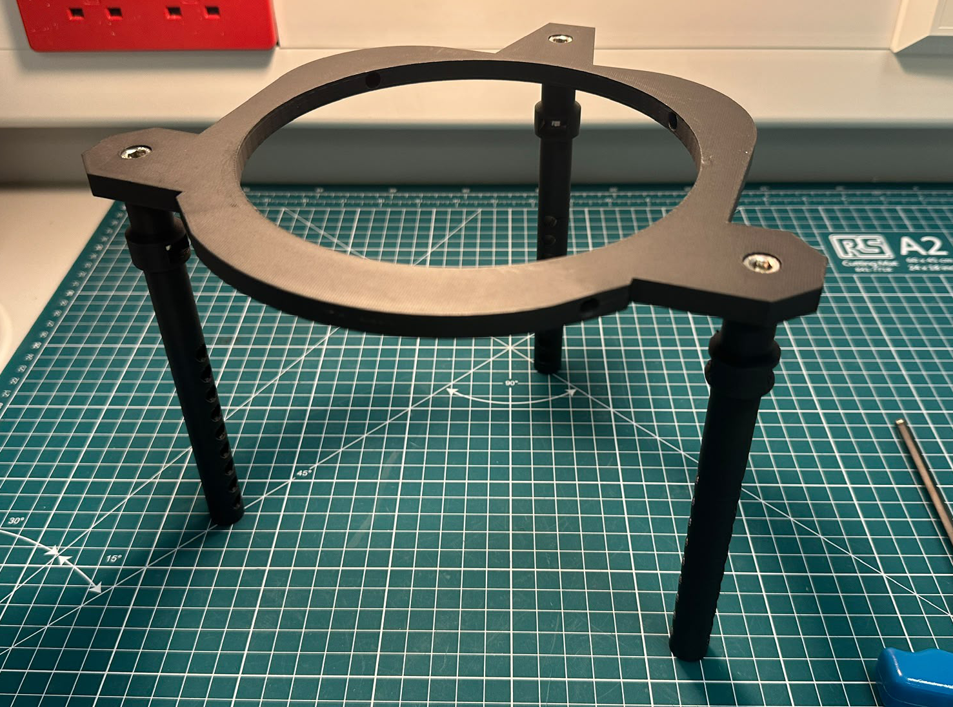
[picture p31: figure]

## Step 4(a)

What you will need:
- LED box holder with LED array attached
- LED box hat
- Assembly of LED canopy to internal posts
- M6x16 mm bolt (x1)

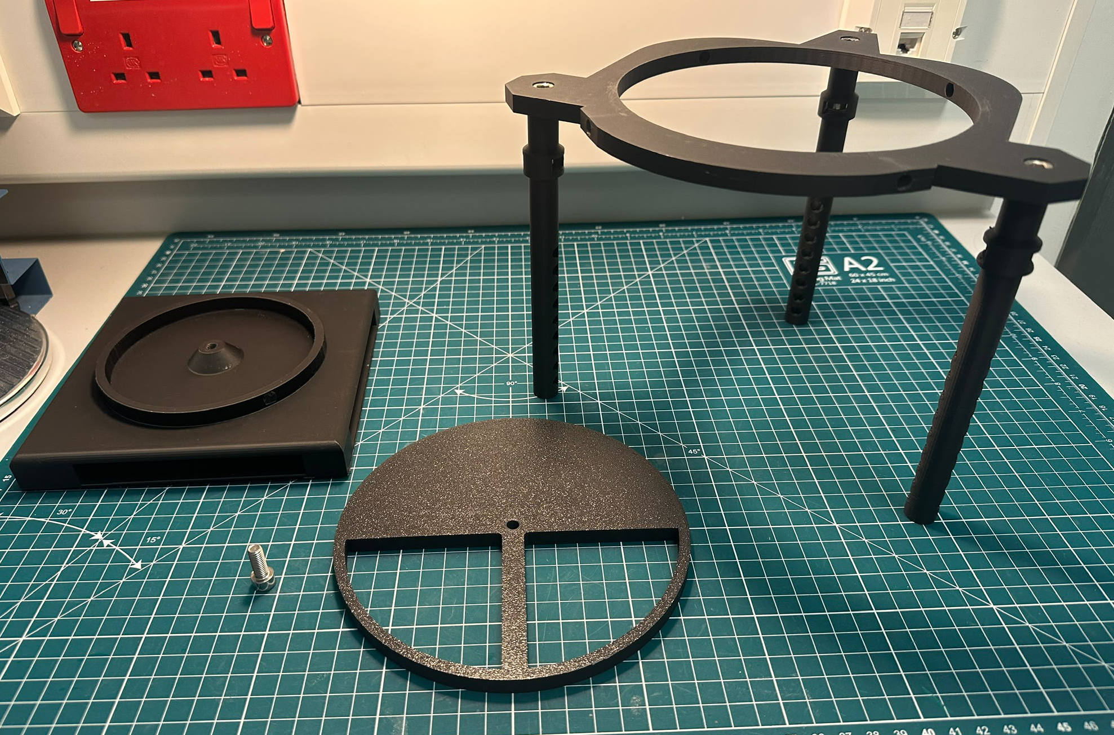
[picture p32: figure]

## Step 4(b)

TODO:
1. Screw the M6x16 mm bolt into the LED box hat

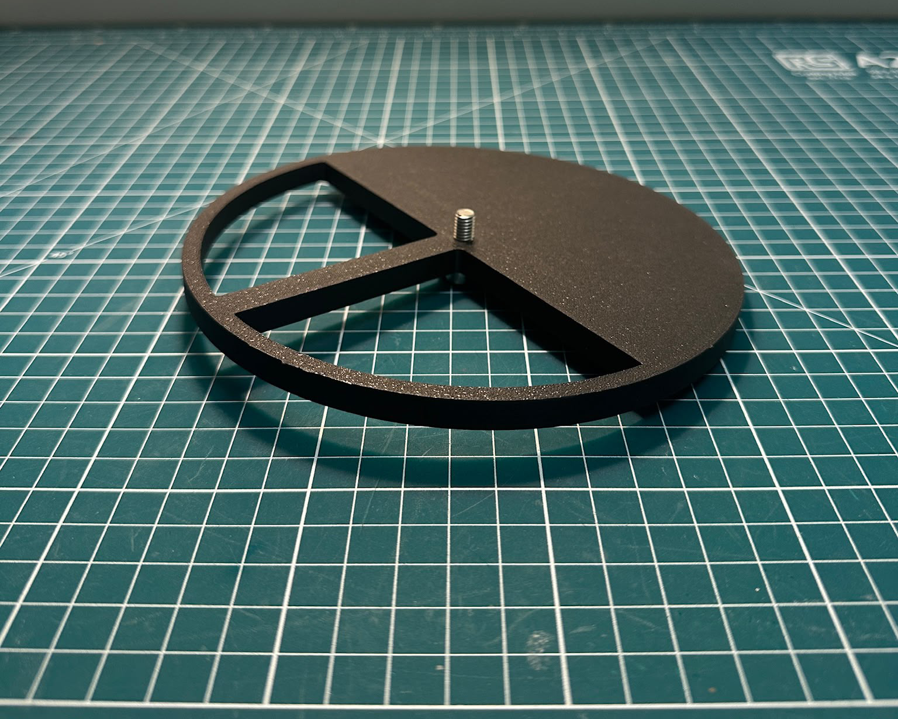
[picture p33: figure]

## Step 4(c)

TODO:
1. Position the components into the following layout.

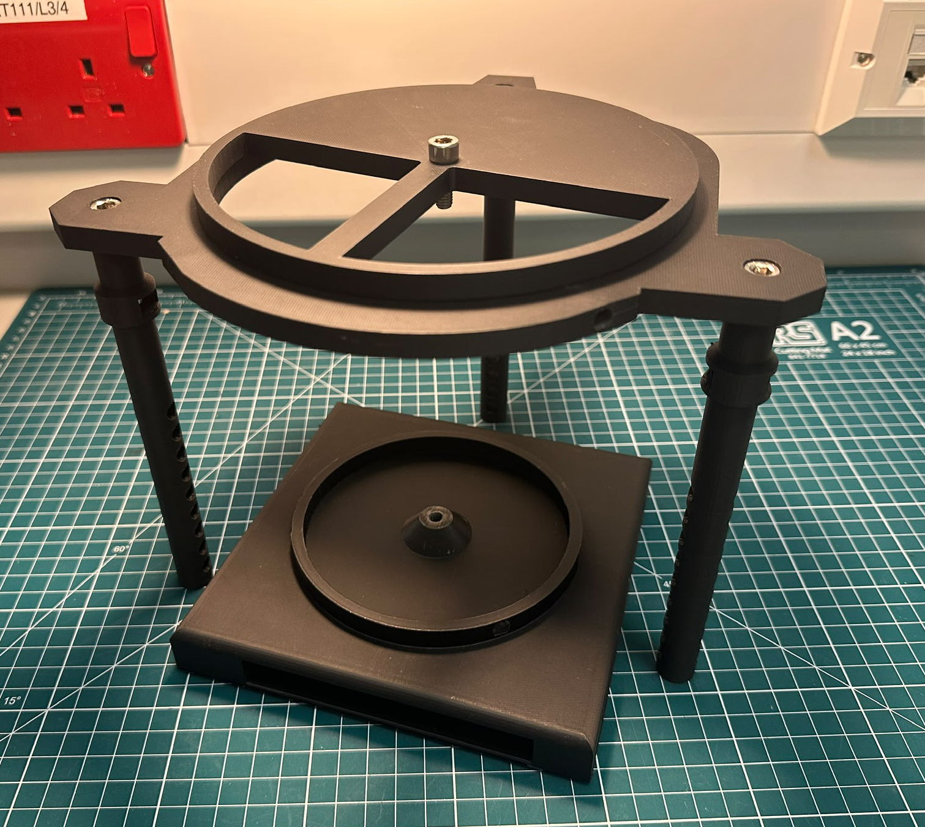
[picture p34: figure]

## Step 4(d)

TODO:
1. Lift the LED box holder up and twist the LED box hat on top until tightly secured.

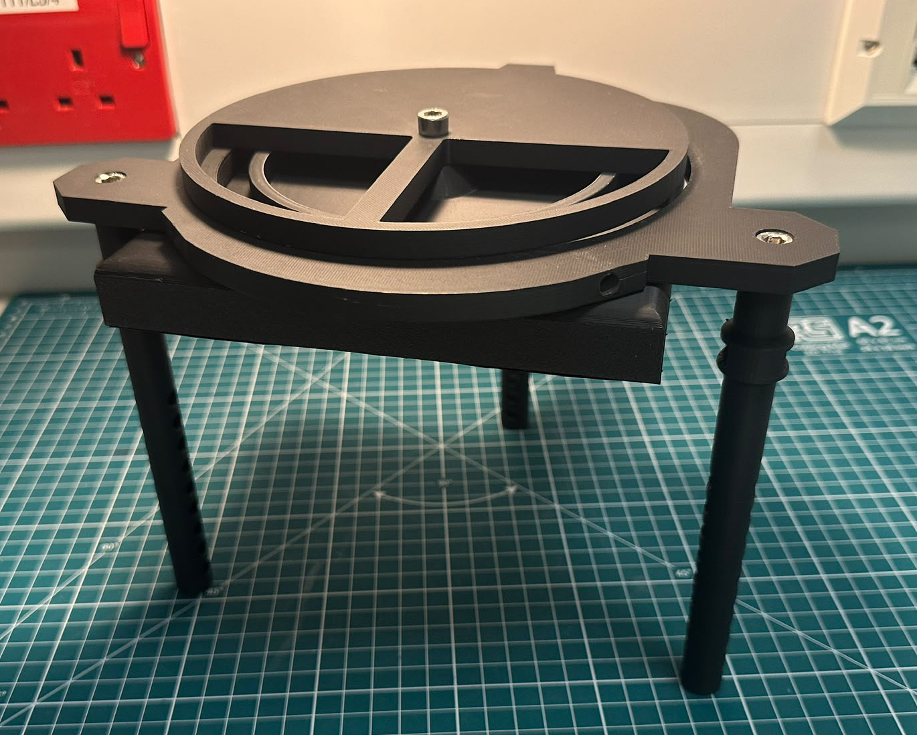
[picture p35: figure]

## Step 4(e)

TODO:
1. The LED array should now be secured in the Z-axis on the canopy and translatable in X and Y axes.

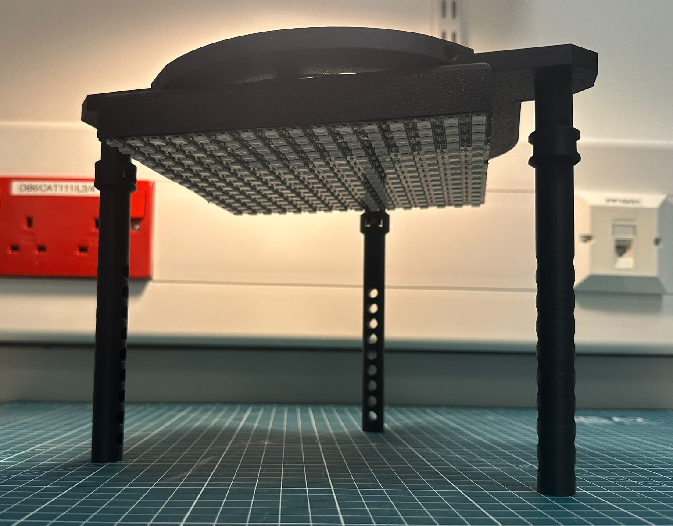
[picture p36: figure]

## Step 5(a)

What you will need:
- Microscope base plate and external posts assembly
- Illuminator canopy and internal posts assembly

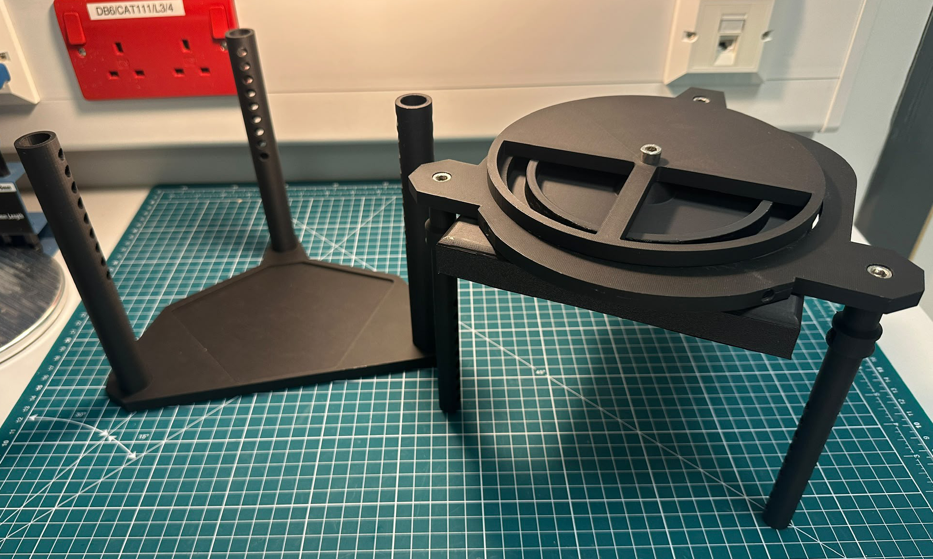
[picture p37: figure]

## Step 5(b)

TODO:
1. Insert the internal posts into the external posts.

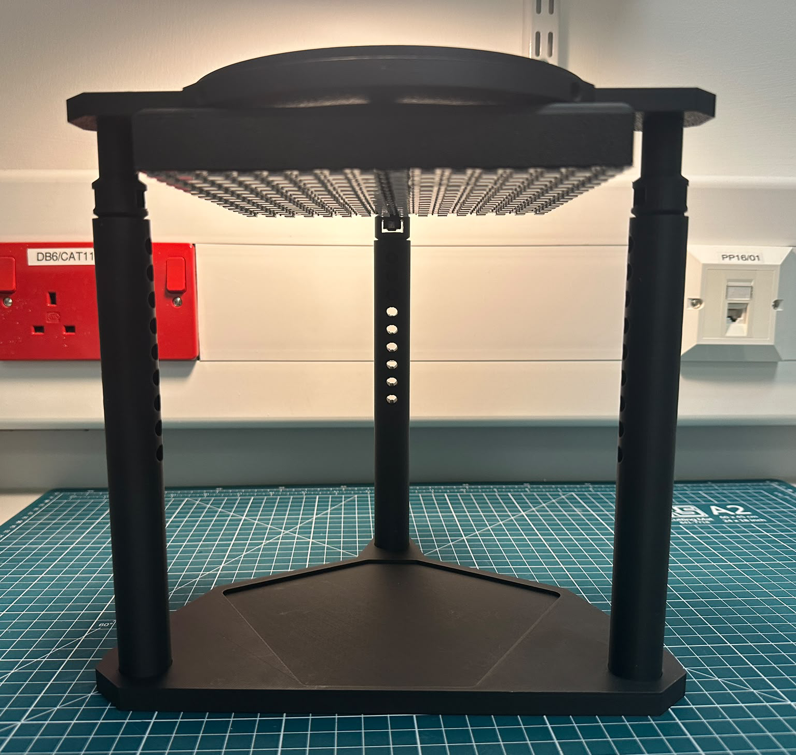
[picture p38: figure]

## Step 6(a)

What you will need:
- Full illuminator assembly
- M6x20 mm bolts (x3)

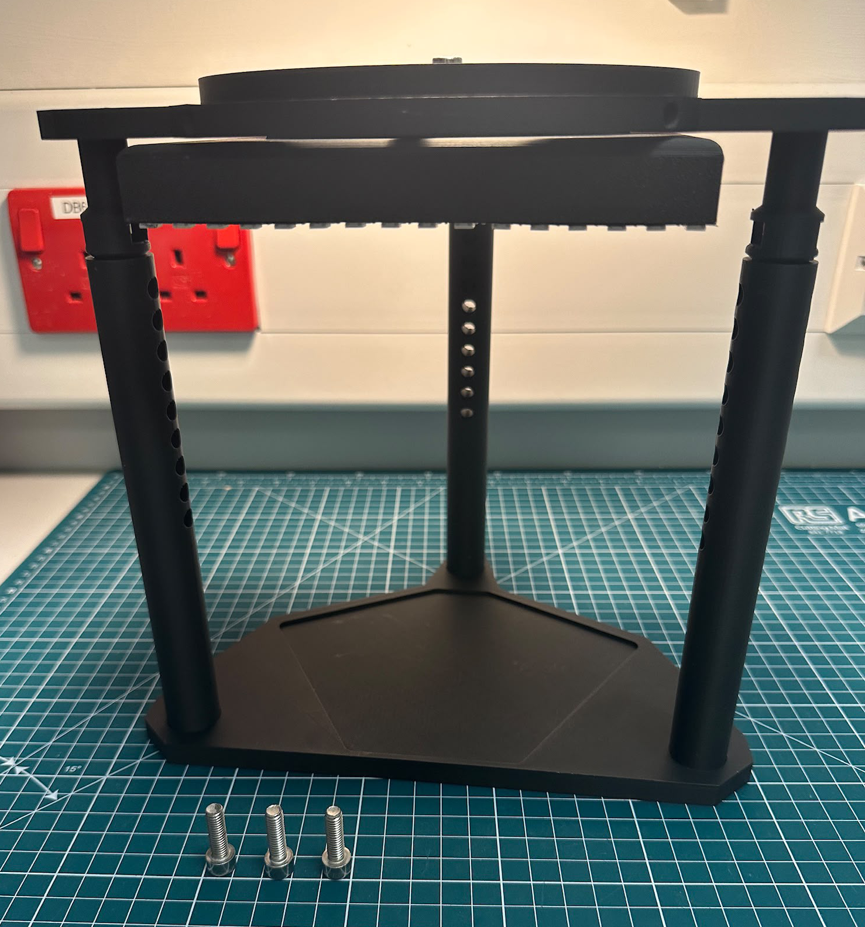
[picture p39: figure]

## Step 6(b)

TODO:
1. Insert the M6x20 mm bolts through the posts for a fixed LED height.
Note:
- The height can be further adjusted once the microscope is attached and is measured from the LED array to the sample plane.

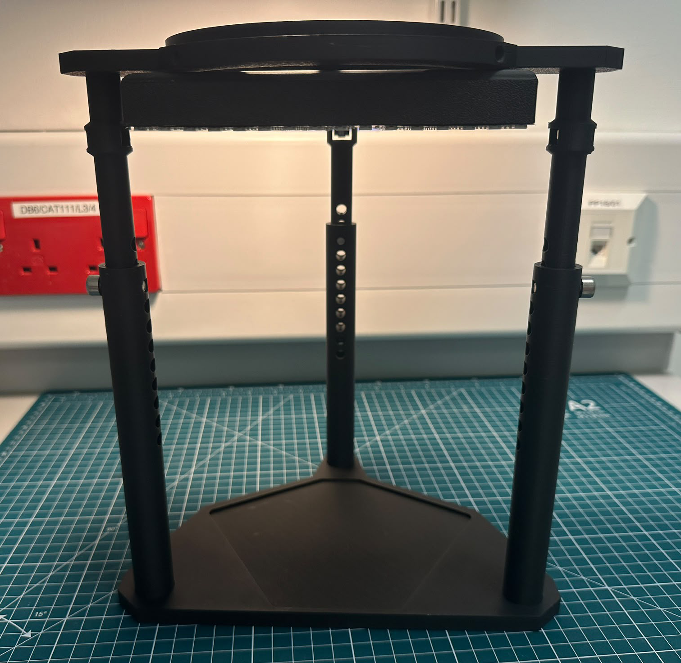
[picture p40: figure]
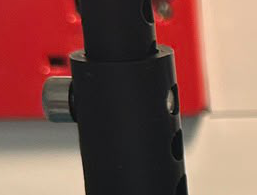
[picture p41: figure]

## Finishing Video

TODO:
1. You should now be able to translate the LED array as seen in this demo video.

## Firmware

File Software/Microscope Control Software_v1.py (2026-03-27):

################################################
# Relaunch as root (keeping X11 env) + grant access
################################################
import os, sys, subprocess, pathlib

# Ensure DISPLAY/XAUTHORITY exist (helps under XRDP)
user_home = str(pathlib.Path.home())
os.environ.setdefault("DISPLAY", os.environ.get("DISPLAY", ":0"))
os.environ.setdefault("XAUTHORITY", os.path.join(user_home, ".Xauthority"))

if os.geteuid() != 0:
    # Allow root to connect to the current X server (run before sudo)
    try:
        subprocess.run(["xhost", "+SI:localuser:root"],
                       check=False, stdout=subprocess.DEVNULL, stderr=subprocess.DEVNULL)
    except Exception:
        pass

    print("Not running as root. Restarting with sudo -E ...")
    # Re-exec as root, preserving env (incl. DISPLAY/XAUTHORITY)
    os.execvp("sudo", ["sudo", "-E", sys.executable] + sys.argv)

################################################
# Main Libraries
################################################

import tkinter as tk
from tkinter import ttk
from rpi_ws281x import PixelStrip, Color
import time
import RPi.GPIO as GPIO
GPIO.setwarnings(False)

################################################
# LED Strip Configuration
################################################
LED_COUNT = 256        # 16x16 = 256 LEDs
LED_PIN = 18           # GPIO pin (must support PWM! GPIO18 is normally used)
LED_FREQ_HZ = 800000   # LED signal frequency in Hz (usually 800kHz)
LED_DMA = 10           # DMA channel to use for generating signal (try 10)
LED_BRIGHTNESS = 255   # Brightness 1-255 [Dark -> Bright]
LED_INVERT = False     # True to invert the signal if required (NPN transistor level shift)
LED_CHANNEL = 0        # 0 or 1 depending on pin (Set to '1' for GPIOs 13, 19, 41, 45 or 53)

# Camera trigger pin (BCM numbering)
CAMERA_TRIGGER_PIN = 16
GPIO.setmode(GPIO.BCM)
GPIO.setup(CAMERA_TRIGGER_PIN, GPIO.OUT, initial=GPIO.LOW)

################################################
# Initialise LED Strip
################################################
strip = PixelStrip(LED_COUNT, LED_PIN, LED_FREQ_HZ, LED_DMA, LED_INVERT, LED_BRIGHTNESS, LED_CHANNEL)
strip.begin()
strip.setBrightness(LED_BRIGHTNESS)

################################################
# Stepper Motors (28BYJ-48 - half-step)
################################################
MOTOR1_PINS = [4, 17, 27, 22]    # Z - Motor
MOTOR2_PINS = [10, 9, 11, 0]     # X - Motor
MOTOR3_PINS = [5, 6, 19, 26]     # Y - Motor

for p in MOTOR1_PINS + MOTOR2_PINS + MOTOR3_PINS:
    GPIO.setup(p, GPIO.OUT)
    GPIO.output(p, GPIO.LOW)

# 8-step half-step sequence
SEQ_HALF_FWD = [
    [1,0,0,0],
    [1,1,0,0],
    [0,1,0,0],
    [0,1,1,0],
    [0,0,1,0],
    [0,0,1,1],
    [0,0,0,1],
    [1,0,0,1]]

SEQ_HALF_BWD = list(reversed(SEQ_HALF_FWD))

# 28BYJ-48: 512 cycles * 8 half-steps = 4096 half-steps ≈ 1 output-shaft revolution
STEPS_PER_REV_CYCLES = 512

# Fixed motor timing - change here if needed.
# If motors stall increase to 1.5-2.5 ms
# If motors are smooth or you want to focus on speed, try 0.7-0.8 ms
### DON'T GO BELOW 0.5 ms
MOTOR_STEP_DELAY_MS = 1.0 # ms per half-step (blocking)

def _deenergise(pins):
    for p in pins:
        GPIO.output(p, GPIO.LOW)

def _run_motor_blocking(pins, seq, cycles, delay_ms):
    """Blocking motor move (no threading)."""
    delay = max(0.0005, float(delay_ms)/1000.0)  # safety floor
    for _ in range(int(cycles)):
        for halfstep in range(8):
            for ch in range(4):
                GPIO.output(pins[ch], seq[halfstep][ch])
            time.sleep(delay)
    _deenergise(pins)

################################################
# Global State
################################################
led_states = [False] * LED_COUNT
led_buttons = []
buttons_by_index = {} # Map LED index to its corresponding GUI button

################################################
# Helper Functions
################################################
def led_index(row, col):
    """Map (row, col) to 1D index for zig-zag wiring:
    even rows (0,2,4,...14) run right -> left
    odd rows (1,3,5,...13) run left -> right"""
    if row % 2 == 0:
        return row * 16 + (15 - col)
    else:
        return row * 16 + col

def get_color():
    choice = color_var.get()
    if choice == 'Red':
        return (255, 0, 0)
    elif choice == 'Green':
        return (0, 255, 0)
    elif choice == 'Blue':
        return (0, 0, 255)
    elif choice == 'Purple':
        return (128, 0, 128)
    elif choice == 'Orange':
        return (255, 165, 0)
    elif choice == 'Cyan':
        return (0, 255, 255)
    elif choice == 'RGB':
        return (255, 255, 255)
    else:
        return (0, 0, 0) # fallback

def on_color_change(event=None):
    print(f'Color changed to: {color_var.get()}')

def get_timing_values():
    try:
        exposure = int(exposure_entry.get())
    except ValueError:
        exposure = 100
    try:
        capture = int(capture_entry.get())
    except ValueError:
        capture = 10
    return exposure, capture

def _fmt_secs(s):
    m = int(s // 60)
    s = int(s % 60)
    return f'{m:02d}:{s:02d}'

def _update_status(k, N, elapsed, eta):
    pct = (k / N) * 100 if N else 0
    status_var.set(f'LED {k}/{N} ({pct:5.1f}%) Elapsed: {_fmt_secs(elapsed)} ETA: {_fmt_secs(eta)}')
    progress.configure(maximum=100, value=pct)
    root.update_idletasks()

# ----- LED Orientation Controls -----
ROTATION = 90        # {0, 90, 180, 270}
FLIP_H = False
FLIP_V = False

def _apply_orientation(r, c):
    if ROTATION == 0:
        rr, cc = r, c
    elif ROTATION == 90:
        rr, cc = c, 15 - r
    elif ROTATION == 180:
        rr, cc = 15 - r, 15 - c
    elif ROTATION == 270:
        rr, cc = 15 - c, r
    else:
        rr, cc = r, c
    if FLIP_H:
        cc = 15 - cc
    if FLIP_V:
        rr = 15 - rr
    return rr, cc

def gui_to_strip_index(r, c):
    rr, cc = _apply_orientation(r, c)
    return led_index(rr, cc)

# ----- Brightness Controls -----
def _apply_brightness(v: int):
    v = max(1, min(int(v), 255))
    strip.setBrightness(v)
    strip.show()
    return v

def on_brightness_slider(val=None):
    v = int(float(val))
    v = _apply_brightness(v)
    brightness_var.set(v)
    brightness_entry_var.set(str(v))

def on_brightness_entry(_event=None):
    try:
        v = int(brightness_entry_var.get())
    except ValueError:
        v = brightness_var.get()
    v = _apply_brightness(v)
    brightness_var.set(v)
    brightness_entry_var.set(str(v))

def validate_entry(new_val):
    if new_val == '':  # allow temporary blank while typing
        return True
    if new_val.isdigit():
        v = int(new_val)
        return 1 <= v <= 255
    return False

# ----- Stepper Motor Controls -----
def _on_step_combo(_evt=None):
    try:
        selected_cycles_var.set(int(step_combo.get()))
    except ValueError:
        selected_cycles_var.set(128); step_combo.set('128')

def _get_selected_cycles():
    try:
        return int(selected_cycles_var.get())
    except Exception:
        return 128

def _set_coils(pins, pattern_row):
    for ch in range(4):
        GPIO.output(pins[ch], pattern_row[ch])
    
def _run_two_motors_blocking(pinsA, seqA, pinsB, seqB, cycles, delay_ms):
    """ Step two 28BYJ-48 motors in lockstep (blocking, no threads)."""
    delay = max(0.0005, float(delay_ms)/1000.0) # safety floor
    for _ in range(int(cycles)):
        for hs in range(8): # half-step subphase
            _set_coils(pinsA, seqA[hs])
            _set_coils(pinsB, seqB[hs])
            time.sleep(delay)
    _deenergise(pinsA)
    _deenergise(pinsB)

def _move_sel(pins, seq):
    # wrapper uses the combo-selected cycles
    _run_motor_blocking(pins, seq, _get_selected_cycles(), MOTOR_STEP_DELAY_MS)
    
def _move_two_sel(pinsA, seqA, pinsB, seqB):
    # interleaves the half-steps for both motors so they stay in sync with one another
    _run_two_motors_blocking(pinsA, seqA, pinsB, seqB, _get_selected_cycles(), MOTOR_STEP_DELAY_MS)

################################################
# LED Patterns (index lists) 
# TODO: Put your patterns here
################################################
centralLED = [135]

Circle3 = [119,120,121,
           136,135,134,
           151,152,153]

Circle9 = [73,72,71,70,69,
           85,86,87,88,89,90,91,
           107,106,105,104,103,102,101,100,99,
           116,117,118,119,120,121,122,123,124,
           139,138,137,136,135,134,133,132,131,
           148,149,150,151,152,153,154,155,156,
           171,170,169,168,167,166,165,164,163,
           181,182,183,184,185,186,187,
           201,200,199,198,197]

Circle15 = [22,23,24,25,26,
            43,42,41,40,39,38,37,36,35,
            51,52,53,54,55,56,57,58,59,60,61,
            77,76,75,74,73,72,71,70,69,68,67,66,65,
            82,83,84,85,86,87,88,89,90,91,92,93,94,
            110,109,108,107,106,105,104,103,102,101,100,99,98,97,96,
            113,114,115,116,117,118,119,120,121,122,123,124,125,126,127,
            142,141,140,139,138,137,136,135,134,133,132,131,130,129,128,
            145,146,147,148,149,150,151,152,153,154,155,156,157,158,159,
            174,173,172,171,170,169,168,167,166,165,164,163,162,161,160,
            178,179,180,181,182,183,184,185,186,187,188,189,190,
            205,204,203,202,201,200,199,198,197,196,195,194,193,
            211,212,213,214,215,216,217,218,219,220,221,
            235,234,233,232,231,230,229,228,227,
            246,247,248,249,250]

CircleDF5ring = [104,103,102,
                 118,122,
                 137,133,
                 150,154,
                 168,167,166]

################################################
# Pattern Functions
################################################
def run_trigger_pattern(led_list):
    clear_all()
    time.sleep(0.2)
    exposure, capture = get_timing_values()
    r,g,b = get_color()
    N = len(led_list)
    progress.configure(value=0)
    status_var.set(f'starting... 0/{N}')
    root.update_idletasks()
    t0 = time.time()
    for k, idx in enumerate(led_list, start=1):
        strip.setPixelColor(idx, Color(r, g, b)); strip.show()
        GPIO.output(CAMERA_TRIGGER_PIN, True)
        time.sleep(exposure/1000.0)
        GPIO.output(CAMERA_TRIGGER_PIN, False)
        strip.setPixelColor(idx, Color(0,0,0)); strip.show()
        time.sleep(capture/1000.0)
        elapsed = time.time() - t0
        per_led = elapsed / k
        remaining = max(N - k, 0) * per_led
        _update_status(k, N, elapsed, remaining)
    total = time.time() - t0
    status_var.set(f'Imaging complete. {N}/{N} Total: {_fmt_secs(total)}')
    progress.configure(value=100)
    print('Time taken:', round(total, 3), 'seconds')

def run_hold_pattern(led_list):
    clear_all()
    time.sleep(0.2)
    r,g,b = get_color()
    for idx in led_list:
        strip.setPixelColor(idx, Color(r, g, b))
        led_states[idx] = True
        btn = buttons_by_index.get(idx)
        if btn:
            btn.config(bg=f'#{r:02x}{g:02x}{b:02x}')
    strip.show()

################################################
# Core Functions
################################################
def toggle_led(idx, button):
    led_states[idx] = not led_states[idx]
    if led_states[idx]:
        r,g,b = get_color()
        strip.setPixelColor(idx, Color(r, g, b))
        button.config(bg=f"#{r:02x}{g:02x}{b:02x}")
    else:
        strip.setPixelColor(idx, Color(0, 0, 0))
        button.config(bg="gray")
    strip.show()

def clear_all():
    for i in range(LED_COUNT):
        strip.setPixelColor(i, Color(0, 0, 0))
        led_states[i] = False
    strip.show()
    for btn in led_buttons:
        btn.config(bg="gray")
    GPIO.output(CAMERA_TRIGGER_PIN, GPIO.LOW)
    for pins in (MOTOR1_PINS, MOTOR2_PINS, MOTOR3_PINS):
        _deenergise(pins)

def close_gui():
    clear_all()
    root.destroy()
    GPIO.cleanup()
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

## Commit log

2025-09-03 FPM_GUI_LEDs
    Version 1
    Python script for graphical user interface used to control the LEDs and camera triggering using Raspberry Pi 4 model B.
2026-03-18 Edited Changes
    [C mount Mirror Cover.f3d, C mount Mirror Cover.step, C mount Mirror Cover.stl, Camera Adapter.f3d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]
2026-06-23 Removal of STL file
    [OpenFlexure_microscope_stand.stl]
2026-06-29 Update 3D print layer height from 0.2mm to 0.4mm
